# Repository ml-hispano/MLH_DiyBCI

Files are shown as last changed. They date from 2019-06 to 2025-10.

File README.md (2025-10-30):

# MLH_BCI
> :warning: **¡ADVERTENCIA! PROYECTO OBSOLETO**
>
> Este proyecto se considera obsoleto. **Motivo principal:** El módulo Wi-Fi implementado provoca una alta **pérdida de paquetes** de información.
<p align="center">
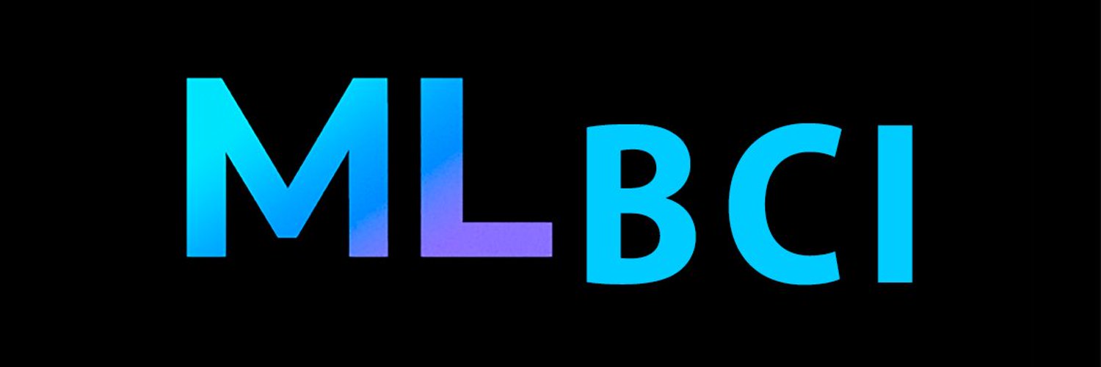
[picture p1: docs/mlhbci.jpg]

</p>

Desarrollo de un electroencefalógrafo EEG, basado en **openBCI** para aplicaciones de **Machine Learning**.

# <a name="introduccion" style="text-decoration:none; color:black;">Introducción</a>

Este es un proyecto de **Javier Morales** para **[MLHispano](https://bit.ly/2Oqingj)**, aquí encontrarás toda la información necesaria para construir tu EEG: Esquemas en Eagle, Gerber files, etc.

*Este proyecto pretende ser un punto de partida donde cualquier individuo de la comunidad de pueda obtener un EEG y desarrollar su BCI a partir de sus propios módelos de machine learning.*

<p align="center">
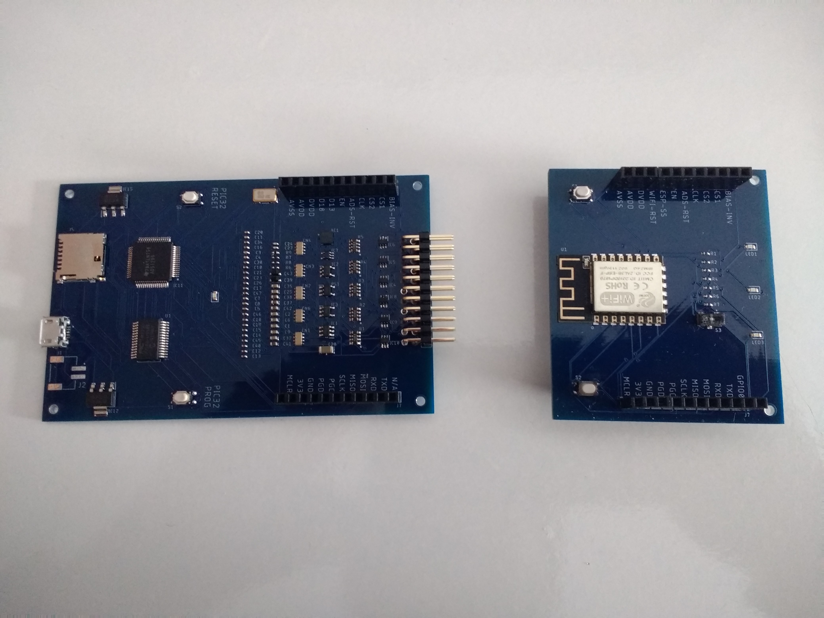
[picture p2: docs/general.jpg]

</p>
A la izquierda el BCI y a la derecha el Wifi.

<p align="center">
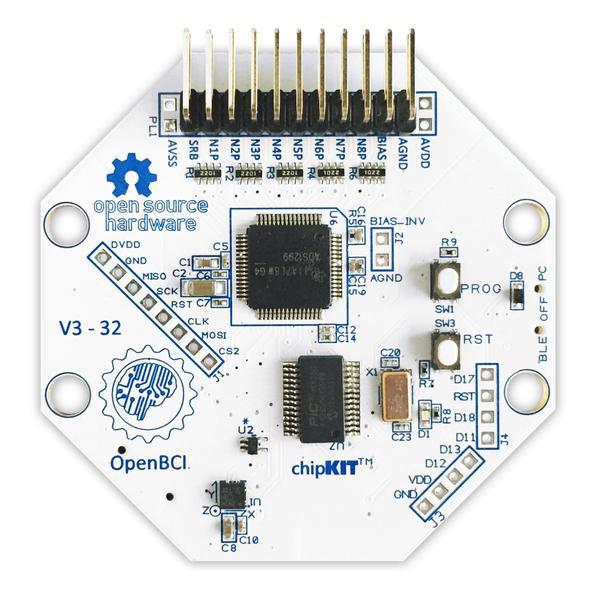
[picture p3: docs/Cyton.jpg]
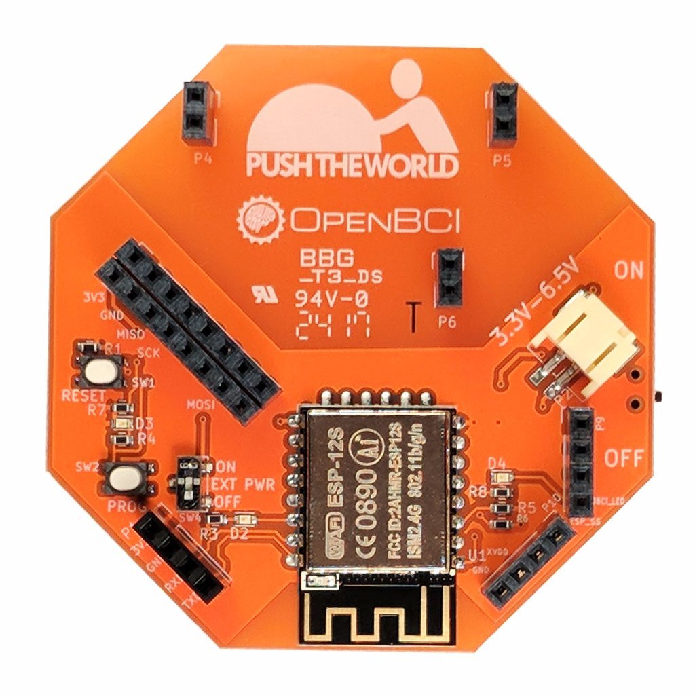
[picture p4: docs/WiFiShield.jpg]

</p>

A la izquierda el OpenBCI y a la derecha el WifiShield. (estos no son nuestros dispositivos)

## Índice

- <a href="#ml-documentacion" >Esquemas, Gerber files, etc.</a>
- <a href="#ml-firmwares">Instalación de los firmwares</a>
- <a href="#ml-handmade">Fabricando el circuito</a>
- <a href="#ml-uso">Uso y manejo del circuito</a>

<!-- - <a href="#ml-agradecimientos" >Agradecimientos</a> -->
<!-- - <a href="#ml-dfrobot">De RFduino a DFRobot</a> -->

## <a name="ml-documentacion" style="text-decoration:none; color:black;">Esquemas, Gerber files, bootloader, firmware, doc.</a>

- [Bootloader del pic32](https://github.com/ml-hispano/MLH_DiyBCI/tree/master/Firmwares%20&%20Bootloader/UDB32-MX2-DIP.hex)
- [Firmware del pic32](https://github.com/ml-hispano/MLH_DiyBCI/tree/master/Firmwares%20&%20Bootloader/DefaultBoard.ino.openbci.hex)
- [Firmware del esp-12E (wifishield)](https://github.com/ml-hispano/MLH_DiyBCI/tree/master/Firmwares%20&%20Bootloader/DefaultWifiShield.2.0.5.bin)
- [Proyecto del MLH_BCI en Eagle (por Javier Morales)](https://github.com/ml-hispano/MLH_DiyBCI/tree/master/Proyecto%20en%20Eagle/MLH_BCI.zip)
- [Gerber files de MLH_BCI (por Javier Morales)](https://github.com/ml-hispano/MLH_DiyBCI/tree/master/Gerber%20files/Gerbers_MLH_BCI.zip)
- [Descargar Interfaz gráfica](https://openbci.com/index.php/downloads)
- [Documentación general de OpenBCI](https://docs.openbci.com/Getting%20Started/00-Welcome)

## <a name="ml-firmwares" style="text-decoration:none; color:black;">Instalación de los firmwares</a>

Para esta instalación no necesitarás RFduino.

El circuito original utilizaba un módulo bluetooth (BLE) **RFduino**, que se encuentra **obsoleto**. Utilizaban un protocolo llamado [Gazell Nordic](https://0w0.pw/nRFGo_SDK/group__nordic__gzll.html), mucho más optimo que el utilizado por el bluetooth de la época. Hasta que llegó WifiShield aportando wifi al sistema.

**WiFiShield** permite omitir fácilmente los puertos serie llenos de latencia y las conexiones Bluetooth de bajo rango. Además, te permite transmitir más rápido y más lejos.

<!--
Un individuo con el alias "alwayswearshats" dijo haber logrado hacer funcionar el openbci con el wifishield sin necesidad de RFduino.
https://youtu.be/NXZVb7ENISs
[fuente](https://openbci.com/forum/index.php?p=/discussion/1773/is-cyton-programming-possible-without-using-bluetooth-dongle#latest)
-->

- Es importante **no acoplar los circuitos (el bci y la wifi) en el momento de programar sus firmwares** o quedarán inservibles.

#### bootloader en el PIC32:
- El procedimiento para subir el bootloader en el pic32 es distinto que para subir el firmware. Necesitarás de un PICkit3 para subir primero el bootloader, para ello puedes utilizar MPLAB IPE. Los pines a utilizar serán **MCLR**, **VDD target**, **Ground**, **PGD** y **PGC**. Todos los pines están incluidos en el circuito y todos son necesarios. El circuito tiene que tener la fuente de alimentación (MicroUSB) enchufado.

<p align="center">
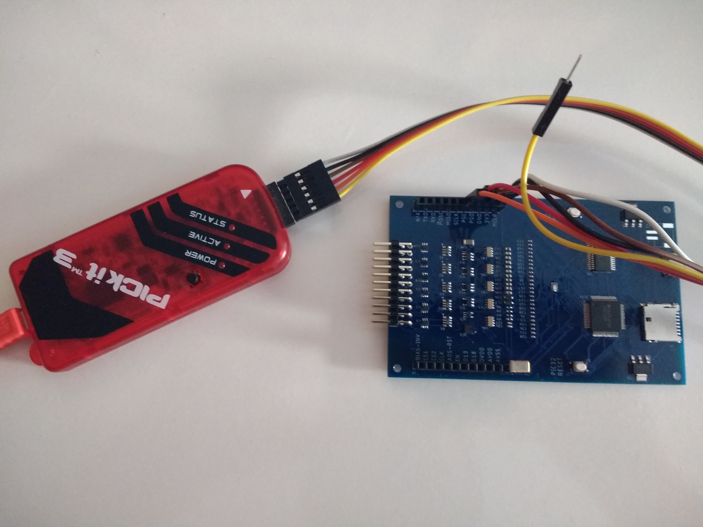
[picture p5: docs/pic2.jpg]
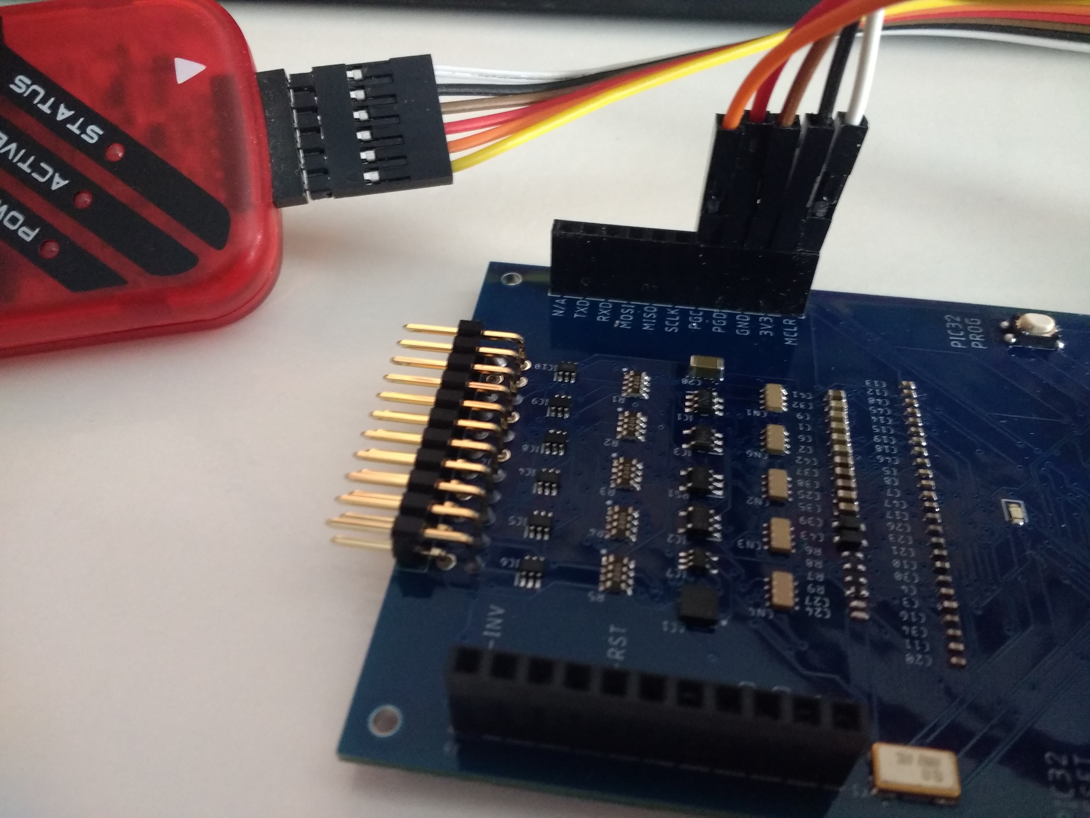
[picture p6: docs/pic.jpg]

</p>

#### firmware en el PIC32:
- **Atención** antes de programar el firmware en el **pic32** tienes que subir el cargador de arranque (**bootloader**).
- Para cargar el firmware en el pic32 necesitarás de un adaptador FTDI, para ello puedes utilizar Arduino IDE, esptool o pic32prog. Los pines a utilizar serán **TXD a RXD** y **RXD a TXD**. El circuito tiene que tener la fuente de alimentación (MicroUSB) enchufado.

#### firmware en WifiShield:
- Para programar el firmware en el circuito equivalente a wifishield necesitarás un adaptador FTDI para programar el firmware del **esp8266 ESP-12E o ESP-12F**, para ello puedes utilizar esptool-gui, esptool, Arduino IDE, etc. Los pines a utilizar pueden variar, dependiendo de si estás utilizando un esp-12E o un kit development con este esp12E integrado, pero en definitiva VCC y GND suelen ser necesarios. Al igual que sucede con el pin DTR de tu FTDI que quizás encuentres oculto en la parte trasera.

- Deberás conectar **DTR a GPIO0**, **RTS a WIFI-RST**, **TXD a RXD** y **RXD a TXD** para subir el firmware. [Fuente](https://github.com/espressif/esptool/wiki/ESP8266-Boot-Mode-Selection)

<p align="center">
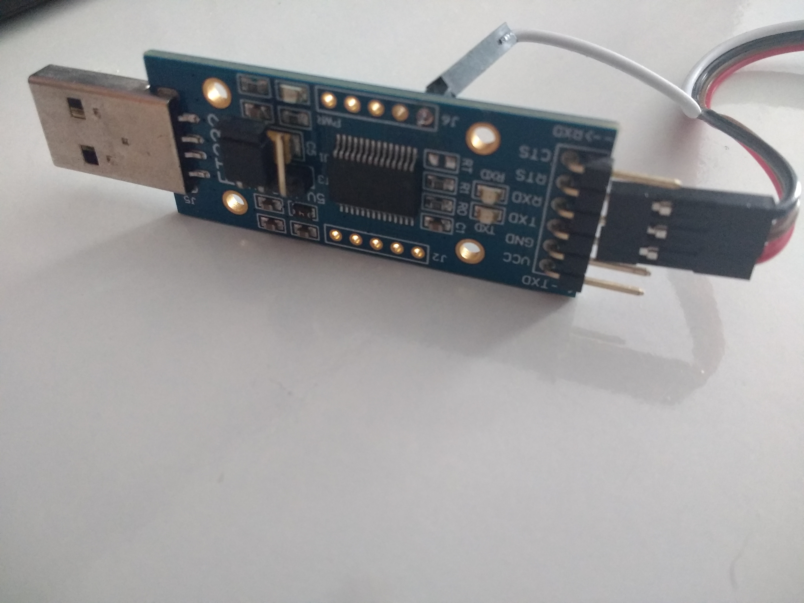
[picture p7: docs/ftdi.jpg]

</p>

- Una vez terminado y habiendo acoplado, ahora sí, los circuitos, deberás conectarte a la red con nombre "OpenBCI-XXXX" y desde el navegador acceder a la siguiente dirección: 192.168.4.1 allí podrás agregar la contraseña de la wifi de tu hogar, para que el dispositivo WifiShield se conecte a la wifi de tu hogar, en lugar de ser un punto de acceso. Entonces podrás ejecutar la aplicación [OpenBCI-GUI](https://openbci.com/index.php/downloads).

<!--
## <a name="ml-dfrobot" style="text-decoration:none; color:black;">De RFduino a DFRobot (TEL0120)</a>

Como hemos dicho, el RFduino está obsoleto, así que he buscado una solucion alternativa si deseas utilizar el bluetooth. La solución viene de la mano de DFRobot, que vende un [módulo BLE 4.1](https://www.dfrobot.com/product-1647.html?search=tel0120&description=true) con el mismo procesador que utilizaba  RFduino, el ARM Cortex M0. Por lo que el firmware debería funcionar.
-->

## <a name="ml-uso" style="text-decoration:none; color:black;">Uso y manejo del circuito</a>

**Sobretodo recordad utilizar como fuente de alimentación, o bien la conexión micro-USB o la batería, nunca ambos a la vez.**

Para empezar a utilizar tu dispositivo, lo primero que tienes que hacer es conectarte al punto de acceso creado por wifishield. Una vez hecho, deberás navegar a la siguiente url 192.168.4.1 y allí podrás introducir los datos de la wifi de tu hogar o trabajo para que wifishield se conecte a ella. Esto es lo único que tienes que hacer antes de poder empezar a disfrutar de tu EEG.

## <a name="ml-handmade" style="text-decoration:none; color:black;">¿Cómo fabrico el circuito?</a>

Esto es solo un ejemplo de lo que debes hacer para mandar a fabricar el circuito, en este caso con [pcbway.es](https://www.pcbway.es/setinvite.aspx?inviteid=292190)

- Dirígete a la página de pcbway, añade las dimensiones de la placa (95 x 60), selecciona 2 capas y pulsa "Cotizar".

<p align="center">
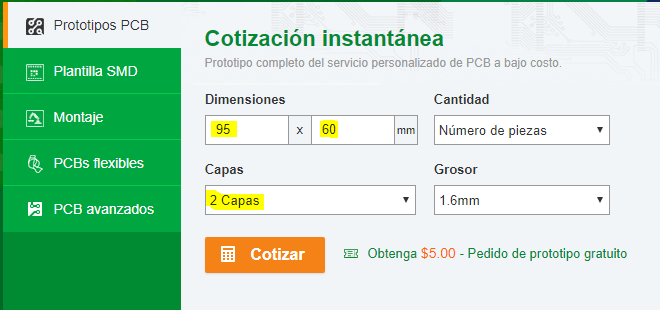
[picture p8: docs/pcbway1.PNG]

</p>

- "Min pista/espacio" debe estar a 6/6 mil y "Min tamaño agujero" debe estar a 0.3 mm aunque el agujero de menor tamaño en el circuito es de 0.35 mm y corresponde a las vias.

- "Máscara de soldadura" se refiere al color de la placa y "Serigrafía" indica el color del texto.

- Cualquier opción en "Acabado superficial", por ejemplo, "Oro por inmersión (ENIG)" incrementará el precio de la placa y aumentará la calidad. No obstante, lo veo innecesario.

- Procesamiento de vias, será por defecto "tenting vias", es decir, vias cubiertas. Así ha sido configurado en el proyecto.

- También es interesante marcar la última opción, "No agregar número extra de producto de pcb a placa".

<p align="center">
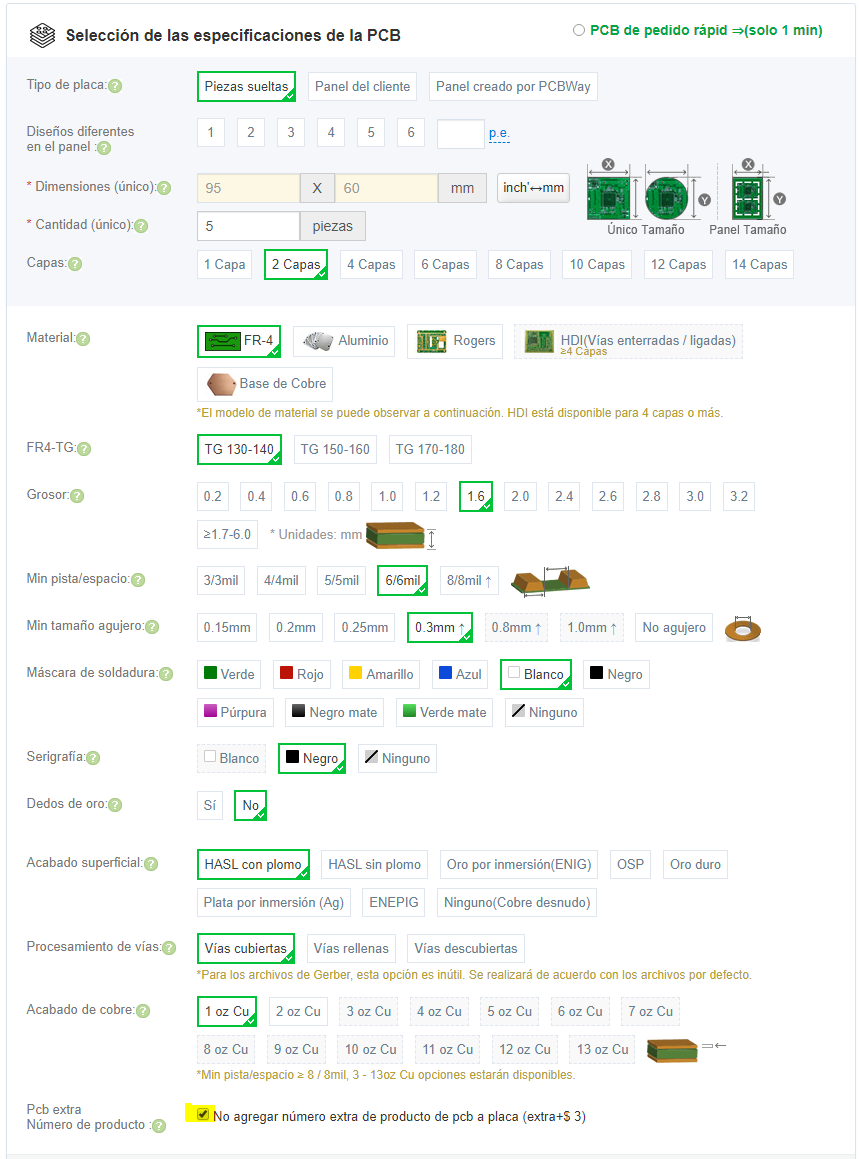
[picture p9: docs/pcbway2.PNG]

</p>

- Es necesario marcar la opción "Plantilla SMD", de este modo os llegará una plantilla de aluminio que podreis poner encima de la placa y pasar la pasta de soldadura por encima con una regla o similar. Podeis escoger el tipo de plantilla que mas os guste, "Con marco" o "Sin marco". Los puntos fiduciales se refieren a las vias, la opción "Ninguno" es correcta.

<p align="center">
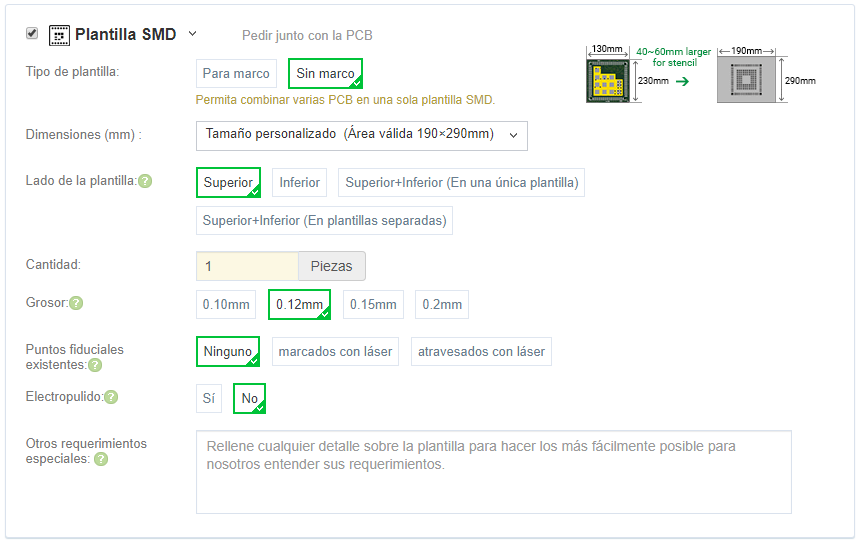
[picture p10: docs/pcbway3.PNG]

</p>

- Clicaremos en calcular, añadiremos el correo electrónico y ya podemos añadir a la cesta. Mas tarde, deberemos añadir el Gerber y el archivo el BOM con los componentes del proyecto. Entonces estará listo para revisión y una vez esta acabe podremos comprarla.

<p align="center">
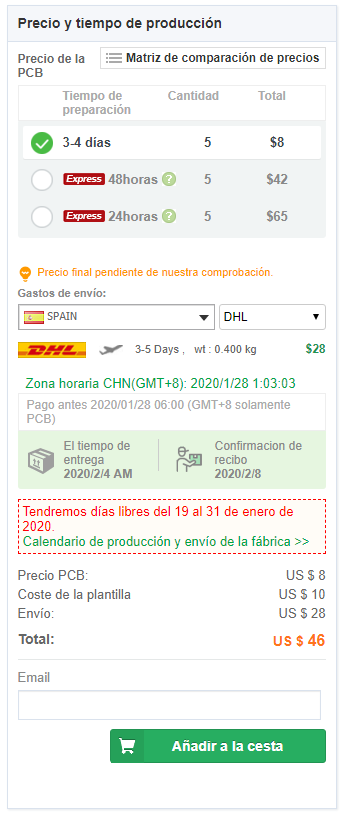
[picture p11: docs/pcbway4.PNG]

</p>

## <a name="ml-agradecimientos" style="text-decoration:none; color:black;">Agradecimientos</a>

- A [OpenBCI](https://openbci.com/)
- A todos los que forman parte de la comunidad MLHispano por su apoyo y en especial a DotCSV.

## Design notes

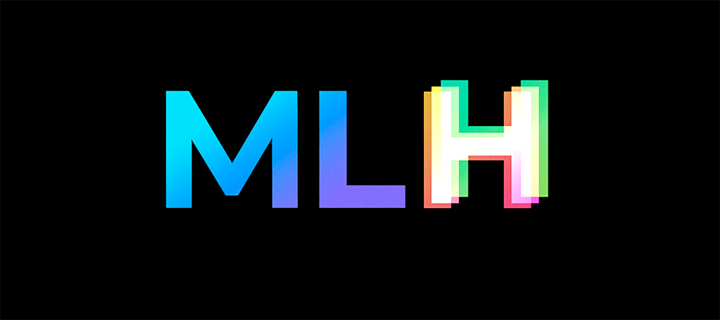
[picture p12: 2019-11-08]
docs/ml-hispano.png

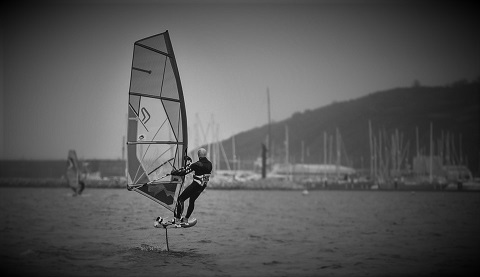
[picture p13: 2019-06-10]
mkdocs/windsurf-hydrofoil.jpg

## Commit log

2019-06-11 Update openbci_cyton.csv
    Cambio de componentes electrónicos.
    [openbci_cyton.csv]
2020-01-27 update Gerber
    [Cyton.csv, MLHBCI_cyton1.xlsx, MLHBCI_daisy.xlsx, MLHBCI_wifi.xlsx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]
